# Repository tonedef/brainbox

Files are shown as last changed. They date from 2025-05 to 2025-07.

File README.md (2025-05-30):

# Disclaimer
Please note! I am not a physcian, nor promising that this device will achieve  positive results of any kind, nor promising that it will do no harm, nor that the device will work exactly as intended. For example, it does use pulsing light/sound which may or may not adversely affect people with epilepsy or other neurological conditions. *Anyone* choosing to build or use this device in part or in full, should consult with their physician first. Anyone who builds or uses this device or utilizes any information presented here, agrees to assume *all* risks and responsibilities. DISCUSS ALL MEDICAL ISUES WITH YOUR PHYSICIAN FIRST

# What is Memini?
Memini is a simple device that produces 40Hz audio and light pulses designed to delay and slow the progression of Alzheimer's/dementia. It's based on promising research done at MIT: 
https://news.mit.edu/2022/small-studies-40hz-sensory-stimulation-confirm-safety-suggest-alzheimers-benefits-1213 (again, I cannot ensure that this will happen.  There are ongoing clinic trials for this, and I have no guarantee that the designs here will be able to achieve that)

It's meant to be as simple as possible for anyone to use. A dimmer to control how bright the light is, a volume control for the sound, and a single button to start/stop the device. It also has a web interface accessible thru WiFi, and the code can be upgraded/modified to support all kinds of things such as:
- making it an alarm clock, so that it runs without user intervention
- tracking usage
- playing reminders for other mental activities
- Repurposing for anything else that could use a couple of buttons and a mono audio output

The MCU being used is a Wemos S2 mini board. While you can use a Wemos C3, or an older D1 (code changes required), the S2 is ideal, as it includes a DAC output which makes it easy to modify the existing on/off square wave audio pulse to support significantly more audio options thru software upgrades.

It's designed using pre-built dev boards and a few through-hole components to make it easy for hobbyists to make. The most challanging thing to build will be the housing, but really anything box like can be used for that.

# Getting started
Aquire the components.

## Electronic component BOM

- 1x PCB board. Send the grb_v_x_x.zip to your PCB mfg. This is the latest confirmed [build](https://github.com/tonedef/Memini/blob/main/KiCad/40Hz_S2/grb_v_0_3.zip)
- 1x [Wemos S2 mini](https://www.amazon.com/HiLetgo-ESP32-S2FN4R2-ESP32-S2-Type-C-Connect/dp/B0B291LZ99)
- 1x  N-Channel logic level MOSFET [CSD19531KCS](https://www.digikey.com/en/products/detail/texas-instruments/CSD19531KCS/4437459). If you're using a short LED strip (< 400mm), you can get away with generic MOSFETs, like the ubiquitous [IRF540](https://www.amazon.com/dp/B0CBKGPJML), which I've tried sucessfully.
- 1x 100 Ohm resistor a [kit](https://www.amazon.com/Resistors-Assortment-Electronic-Components-Experiments/dp/B09SFCF5XY/) is probably the best bet for this if you don't have one already
- 1x 10k Ohm resistor a [kit](https://www.amazon.com/Resistors-Assortment-Electronic-Components-Experiments/dp/B09SFCF5XY/) is probably the best bet for this if you don't have one already
- 1x 1n4007 Diode. Again, a [kit](https://www.amazon.com/HiLetgo-100pcs-Schottky-Rectifier-Assorted/dp/B07VHMCJK1/) if you don't have one already
- 1x 10k Ohm 15mm PCB vertical [potentiometer](https://www.amazon.com/dp/B0DN1DHWLR).
- 1x 20mm Rotary [encoder](https://www.amazon.com/dp/B07D3DF8TK) (with or without switch). 
- 1x 0.96in 4 pin [I2C display](https://www.amazon.com/MakerFocus-Display-Communication-SSD1315-Raspberry/dp/B0DR2CMYGM)
- 1x PAM8302 [audio dev board](https://www.amazon.com/Audio-Development-Tools-Adafruit-Amplifier/dp/B00PY2YSI4)
- 5V [LED strip](https://www.amazon.com/dp/B0DPKMQNJJ) (pay attention to the Voltage, most are 12V). You can use any color, but I'd recommend a warm white like 3000K.
- 2x 6×6×9mm [Momentary Tactile Tact Push Button Switches](https://www.amazon.com/dp/B07CGCPGPT?th=1)
- 1x Small 4 Ohm [speaker](https://www.amazon.com/dp/B0CCP2Q168)
- 1x [5V power supply](https://www.amazon.com/100-240V-Extension-Replacement-5-5x2-5mm-Security/dp/B0DGFSQS97) walwart
- 1x DC [jack](https://www.amazon.com/dp/B07CTCLKPP) that fits your 5V walwart
- 2x M2x6mm standoffs. A [kit](https://www.amazon.com/300pcs-Standoff-Column-Spacer-Assortment/dp/B07B9X1KY6/) is good, if you don't have one already.
- Assorted 2.54mm male and female [headers](https://www.amazon.com/dp/B0774VBJ3J) (most/all of these should already be included in the components above). You can of course use [JTS-XH](https://www.amazon.com/Taiss-560PCS-Connector-Adapter-Housing/dp/B09ZTWCZ3K) connectors for the power in, LED out, and  audio out, or just wire them directly.
 
 ## Case
 There's plenty of ways to do this. The easiest is to just a get a cast acrylic box that's roughly 4"x4"x4" and has roughly 1/8" (3mm) thick walls. I simply made boxes out of wood I had lying around, and grabbed a cheap piece of 1/8" scrap cast acrylic from TAP Plastics for the face plate. Cast acrylic usually has a paper backing as opposed to a plastic film. Cast acrylic is generally easier to machine.

 # Assembly
 ## software
 You will need to know how to connect your Wemos S2 to your PC and upload the code to it. There are plenty of tutorials on how to do this. The board needs to be in the [DFU mode](https://www.wemos.cc/en/latest/tutorials/s2/get_started_with_arduino_s2.html) to get picked up, and you need the espressif boards in your Arduino IDE, along with a bunch of libraries:
 - ESP32 boards [installation](https://randomnerdtutorials.com/installing-the-esp32-board-in-arduino-ide-windows-instructions/)
 - ezButton (library from ArduinoGetStarted.com)
 - ESP Rotary (library from Lennart Hennigs)
 - Adafruit_GFX (library from Adafruit)
 - Adafruit_SSD1306 (library from Adafruit)
  
  Libraries are installed thru the Arudino IDE interface. It's been a while since I installed the things I need, so my appologies if I've missed anything. If you get errors, it should point to what's missing, and you'll have to  look for it and install the library.

  ## hardware (main board)
  - install the female headers for the Wemos board
  - dry fit the male pins to the audio dev board and the PCB (don't solder just yet)
  - solder the male pins to all the dev boards (Wemos, audio, and display). DON'T solder to any of these to the PCB just yet, but do dry fit them to make sure the pins are properly aligned and adjust if needed.
  - if your using connectors for the power in, audio out, and LED out, solder them now
  - solder all the remaining components to the PCB except for the display
  - attach the standoffs to the display.
  - As the OLED 0.96 displays aren't fully standardized on pin placement and mounting holes, the PCB has generous sized mounting holes and pin pads. Fit the display on the PCB and align it.
  - screw in the display's attached standoffs to the PCB
  - keeping the display parallel to the PCB, solder the display pins to the PCB
 
 ## hardware (DC jack, LED, and speaker)

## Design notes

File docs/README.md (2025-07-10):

>[!IMPORTANT]
I am not a physician and make no guarantees about this device's effectiveness, safety, or intended function. It uses pulsing light and sound, which may pose risks for individuals with epilepsy or other neurological conditions. Anyone choosing to build or use this device, in whole or in part, should consult their physician beforehand. By engaging with this device or any related information, you accept full responsibility for all risks. Always discuss medical concerns with your doctor first.

# What is wavebox?
Wavebox is a simple device that produces 40Hz audio and light pulses designed to delay and slow the progression of Alzheimer's/dementia. It's based on promising research done at MIT: 
https://news.mit.edu/2022/small-studies-40hz-sensory-stimulation-confirm-safety-suggest-alzheimers-benefits-1213 

Again, I cannot ensure that this will happen. There are ongoing clinic trials for this, so the efficacy is still being evaluated.

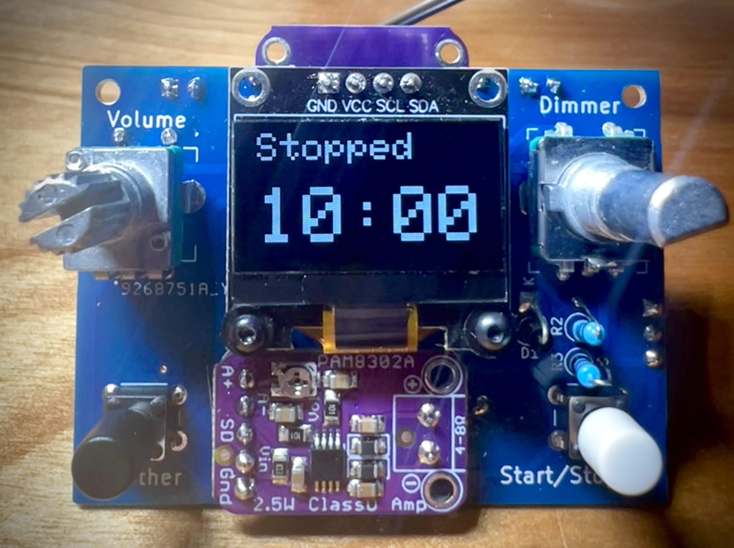
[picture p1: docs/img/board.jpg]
working board


It's meant to be as simple as possible for anyone to use. A dimmer to control how bright the light is, a volume control for the sound, and a single button to start/stop the device (though two other buttons, one on the encoder and one on left side exist for expansion or to repurpose this for any number of other uses, like a radio). It also has a web interface accessible thru WiFi, and the code can be upgraded/modified to support all kinds of things such as:
- making it an alarm clock, so that it runs without user intervention
- tracking usage
- playing reminders for other mental activities
- Repurposing for anything else that could use a couple of buttons and a mono audio output

The MCU being used is a Wemos S2 mini board. While you can use a Wemos C3, or an older D1 (significant code changes required), the S2 is ideal, as the GPIO pin being used to supply the PWM audio (which here is just a simple square wave), is also the DAC output. This makes it easy to switch over to an 8bit DAC output to support significantly more audio options thru software.

It's designed using pre-built dev boards and a few through-hole components to make it easy for hobbyists to make. The most challanging thing to build will be the housing, but really anything box like can be used for that.

# Getting started

## Electronic component BOM
Get all the necessary components for the electronics. You don't have to get the exact brand I've listed, but the values, and footprint of the component is important. I've made a few of these with generic no-name encoders and pots for example. The 0.96" I2C displays all seem to have slight variations in hole/pin placements, which I've tried to account for in the PCB's mounting and through-hole pads.

- 1x PCB board. Send the grb_v_x_x.zip to your PCB mfg. This is the latest confirmed [build](https://github.com/tonedef/wavebox/blob/main/KiCad/40Hz_S2/grb_v_0_3.zip). Also happy to orchestrate a group buy if folks are interested (minimum order is usually 5)
- 1x [Wemos S2 mini](https://www.amazon.com/HiLetgo-ESP32-S2FN4R2-ESP32-S2-Type-C-Connect/dp/B0B291LZ99)
- 1x  N-Channel MOSFETs [IRF540](https://www.amazon.com/dp/B0CBKGPJML) .
- 1x 100 Ohm resistor. A [kit](https://www.amazon.com/dp/B07L851T3V/ref=sspa_dk_detail_0) is probably the best bet for this if you don't have one already
- 1x 10k Ohm resistor (would be in the kit above)
- 1x 1n4007 Diode. Again, a [kit](https://www.amazon.com/HiLetgo-100pcs-Schottky-Rectifier-Assorted/dp/B07VHMCJK1/) if you don't have one already
- 1x 10k Ohm 15mm PCB vertical [potentiometer](https://www.amazon.com/dp/B0DN1DHWLR).
- 1x 20mm Rotary [encoder](https://www.amazon.com/dp/B07D3DF8TK) (with or without switch). 
- 1x 0.96in 4 pin [I2C display](https://www.amazon.com/MakerFocus-Display-Communication-SSD1315-Raspberry/dp/B0DR2CMYGM)
- 1x PAM8302 [audio dev board](https://www.amazon.com/Audio-Development-Tools-Adafruit-Amplifier/dp/B00PY2YSI4)
- 5V [LED strip](https://www.amazon.com/dp/B0DPKMQNJJ) (pay attention to the Voltage, most are 12V). You can use any color, but I'd recommend a warm white like 3000K.
- 2x 6x6x12 Momentary tactile [buttons](https://www.amazon.com/uxcell-6x6x12mm-Momentary-Tactile-Button/dp/B07JLV6WSF/)
- 1x Box of [caps](https://www.amazon.com/Tactile-Button-Plastic-Replacement-Breadboard/dp/B0B52B8S63) (don't need a whole box, but aren't really sold individually usually)
- 1x Small 4 Ohm [speaker](https://www.amazon.com/dp/B0CCP2Q168) (8ohm should also work)
- 1x [5V power supply](https://www.amazon.com/100-240V-Extension-Replacement-5-5x2-5mm-Security/dp/B0DGFSQS97) walwart. You can also just use the USB-C connector on the Wemos S2 mini, which is great for easy reprogramming, but limits the amperage you can draw on the LED out (only an issue if you need more than ~500mA). 
- 1x DC [jack](https://www.amazon.com/dp/B07CTCLKPP) that fits your 5V walwart

- 2x M2x6mm standoffs. A [kit](https://www.amazon.com/300pcs-Standoff-Column-Spacer-Assortment/dp/B07B9X1KY6/) is good, if you don't have one already.
- Assorted 2.54mm male and female [headers](https://www.amazon.com/dp/B0774VBJ3J) (most/all of these should already be included in the components above). You can of course use [JTS-XH](https://www.amazon.com/Taiss-560PCS-Connector-Adapter-Housing/dp/B09ZTWCZ3K) connectors for the power in, LED out, and  audio out, or just wire them directly.
 
 ## Case
 There's plenty of ways to do this. The easiest is to just a get a cast acrylic box that's roughly 4"x4"x4" and has roughly 1/8" (3mm) thick walls. I simply made boxes out of wood I had lying around, and grabbed a cheap piece of 1/8" scrap cast acrylic from TAP Plastics for the face plate. Cast acrylic usually has a paper backing as opposed to a plastic film. Cast acrylic is generally easier to machine.

 # Assembly
 ## software
 You will need to know how to connect your Wemos S2 to your PC and upload the code to it. There are plenty of tutorials on how to do this. The board needs to be in the [DFU mode](https://www.wemos.cc/en/latest/tutorials/s2/get_started_with_arduino_s2.html) to get picked up, and you need the espressif boards in your Arduino IDE, along with a bunch of libraries:
 - ESP32 boards [installation](https://randomnerdtutorials.com/installing-the-esp32-board-in-arduino-ide-windows-instructions/)
 - ezButton (library from ArduinoGetStarted.com)
 - ESP Rotary (library from Lennart Hennigs)
 - Adafruit_GFX (library from Adafruit)
 - Adafruit_SSD1306 (library from Adafruit)
  
  Libraries are installed thru the Arudino IDE interface. It's been a while since I installed the things I need, so my appologies if I've missed anything. If you get errors, it should point to what's missing, and you'll have to  look for it and install the library.

  ## hardware (main board)
  - install the female headers for the Wemos board
  - solder the male pins to all the dev boards (Wemos, audio, and display). DON'T solder to any of these to the PCB just yet, but do dry fit them to make sure the pins are properly aligned and adjust if needed.
  - if your using connectors for the power in, audio out, and LED out, solder them now
  - solder all the remaining components, including the female headers for the Wemos board, to the PCB except for the display
  - attach the standoffs to the display.
  - As the OLED 0.96 displays aren't fully standardized on pin placement and mounting holes, the PCB has generous sized mounting holes and pin pads. Fit the display on the PCB and align it.
  - screw in the display's attached standoffs to the PCB
  - keeping the display parallel to the PCB, solder the display pins to the PCB (they may not protrude all the way thru the board, but that's fine)
 
 ## hardware (front panel)
  - any material can be used, but the easiest is a 1/8" thick 4x4" piece of clear cast acrylic.
  - [SVG and PDF](https://github.com/tonedef/wavebox/tree/main/images) faceplates can either be printed to guide manual cutting or used in CAD for CNC
  - note: the faceplate has offset mounting as opposed to the corners, so that you're not screwing the faceplate into a 45 joint of the housing, assuming you're making this out of wood with faces cut at a 45 degree bevel

 ## hardware (housing)
  - 3/4" 4x18" wood board works
  - cut 4, 4x4 sections at a 45 degree bevel
  - set a bit or a blade to 3/8" deep and run one side of all four sections about 1/8" in from the edge (this will make a 1/8" inset for your faceplate) 
  - in the center of one of the 4x4 pieces, cut a hole for the speaker (check the diameter you need for your speaker, it should be about 2")
  - on the same board as the speaker, cut a small 1/8 hole or so for the LED wires about 1/2 from the top edge in line with the center of the speaker
  - on the same board as the speaker, at the opposite end of the LED hole, cut a mount hole for your DC plug or a slot for a USB cable (if you plan to inset a bottom face into the box, leave enough room to accomodate your plug/cable)
  - glue and/or nail all four boards together so they form a box
  - finish the box however you like

 ## hardware (DC jack, LED, and speaker)
  - leaving the tape on, wrap the LED strip around the top edge of the box and cut the strip at the nearest cut point where the strip doesn't overlap
  - attach wire leads to the LED strip, the DC jack (if using), and the speaker, make them long enough to attach to the PCB with room to spare so you can connect everything easily
  - feed the LED leads thru the hole cut for the LED wires
  - take the tape off the LED strip and tape the strip around the box, then lift up each end of the strip, apply a drop of superglue and press them back down (most tape backings don't hold long term)
  - attach speaker and DC jack to box
  - attach leads to the PCB board
  - attach faceplat to PCB board, and then attach the faceplate to the box

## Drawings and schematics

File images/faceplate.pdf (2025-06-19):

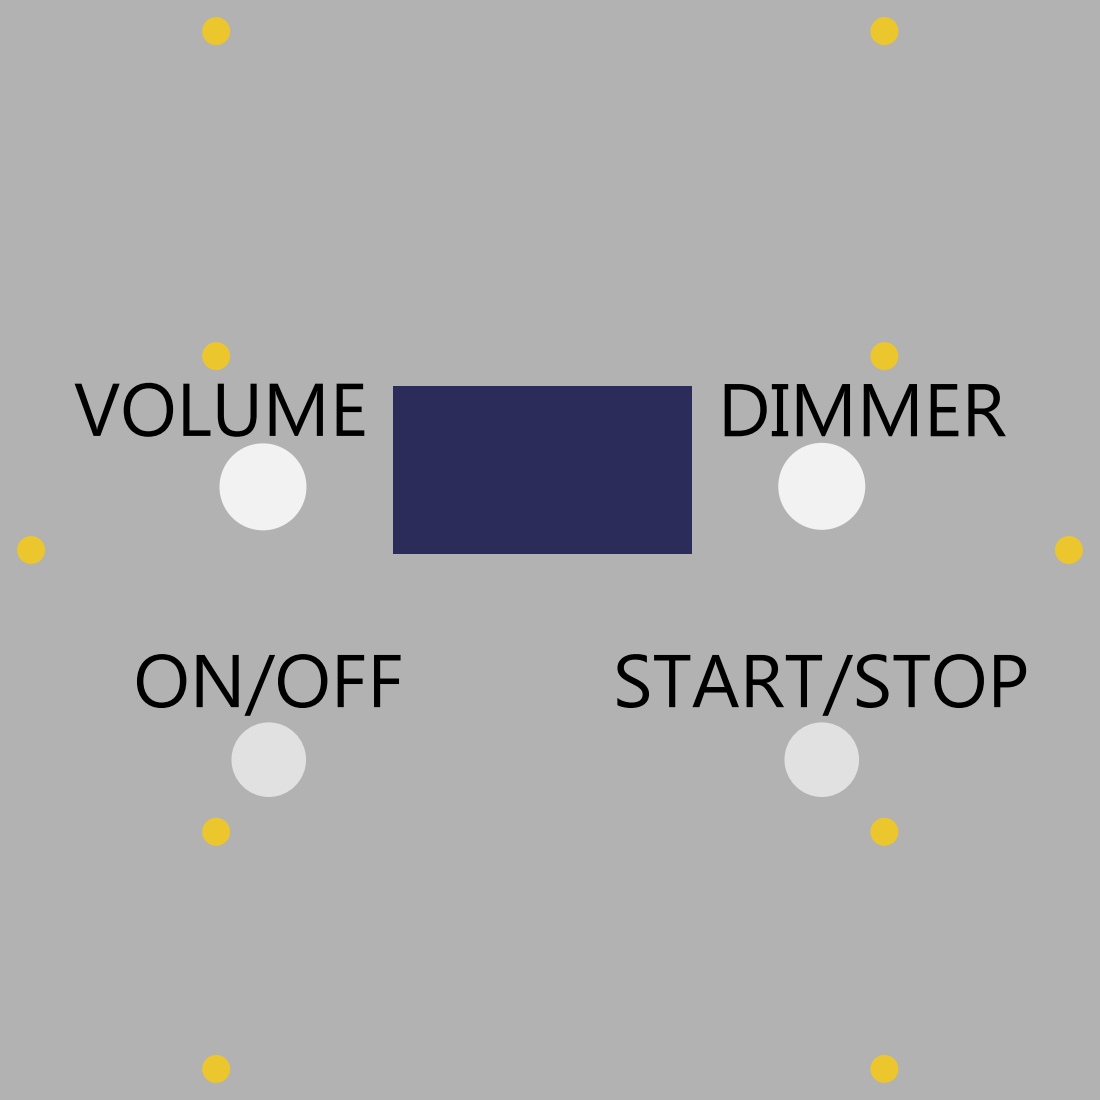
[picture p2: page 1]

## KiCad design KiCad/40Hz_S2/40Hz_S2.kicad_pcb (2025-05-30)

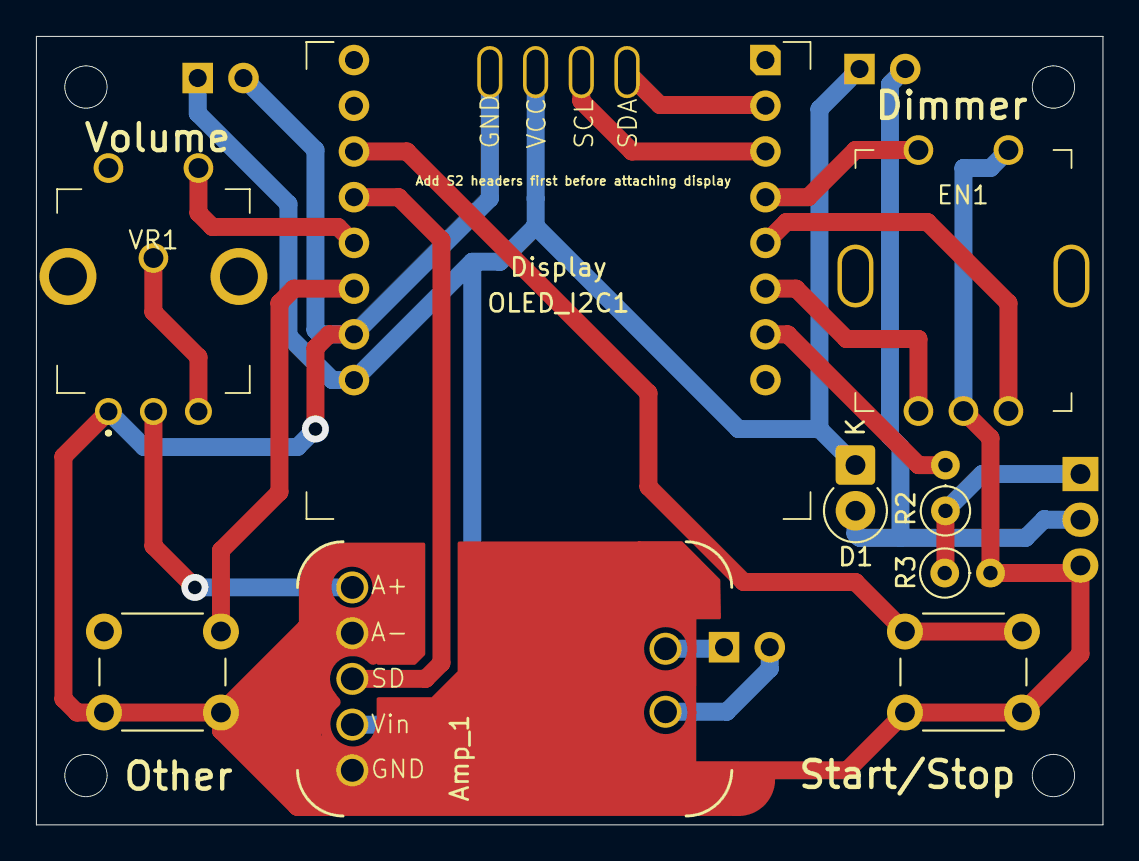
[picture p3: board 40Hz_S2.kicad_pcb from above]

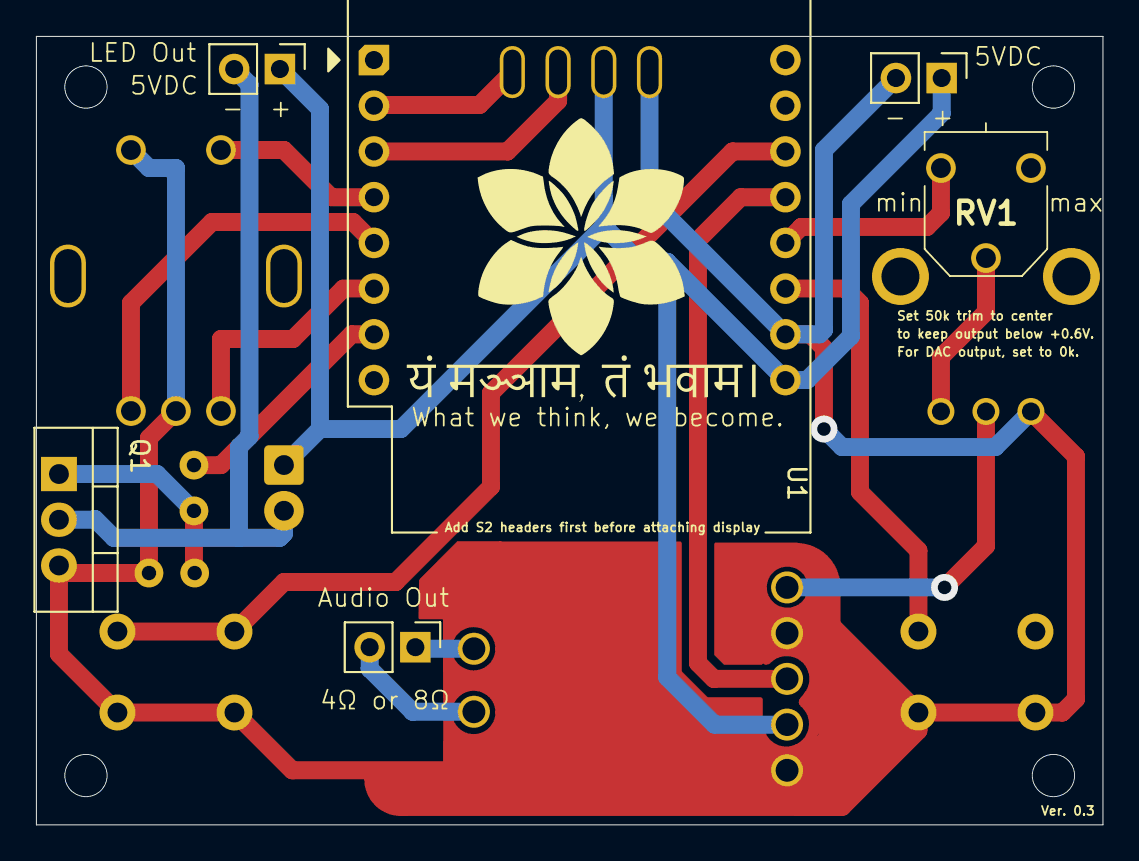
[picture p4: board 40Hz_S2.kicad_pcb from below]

Board: 2 copper layers, 59.2 x 43.8 mm, 15 parts (6 on the bottom side), 18 nets.

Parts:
Amp_1: PAM8302_adafruit
D1: 1N4007; D_DO-41_SOD81_P2.54mm_Vertical_KathodeUp
EN1: Encoder; encoder_20mm_switch
J1: PWR; PinHeader_1x02_P2.54mm_Vertical
J2: Audio; PinHeader_1x02_P2.54mm_Vertical
J3: LED; PinHeader_1x02_P2.54mm_Vertical
OLED_I2C1: Display; OLED_display_I2C_0_96in
Q1: CSD19531KCS; TO-220-3_Vertical
R2: 100; R_Axial_DIN0207_L6.3mm_D2.5mm_P2.54mm_Vertical
R3: 10K; R_Axial_DIN0207_L6.3mm_D2.5mm_P2.54mm_Vertical
RV1: R_Potentiometer_Trim_US; 3306F1103
U1: WeMos_S2_mini; WEMOS_S2_mini_no_inner_row
VR1: 10K Pot; potentiometer_vert_no_switch
other1: Start/Stop; SW_PUSH_6mm_H9.5mm
start/stop1: Start/Stop; SW_PUSH_6mm_H9.5mm

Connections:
5V: Amp_1.4 (Vin), D1.1 (K), J1.1, J3.1, OLED_I2C1.Vcc, U1.9 (VBUS)
Audio: RV1.3, U1.12 (IO18)
Btn1: U1.14 (IO35), start/stop1.1
Btn2: EN1.1, U1.4 (IO7)
Btn3: U1.11 (IO16), other1.1
Enc_A: EN1.A1 (A), U1.6 (IO11)
Enc_B: EN1.B1 (B), U1.5 (IO9)
GND: Amp_1.2 (A-), Amp_1.5 (GND), EN1.2, EN1.GND, J1.2, OLED_I2C1.GND, Q1.3 (S), R3.2, U1.10 (GND), VR1.1, other1.2, start/stop1.2
LED: R2.2, U1.7 (IO12)
unnamed: Amp_1.1 (A+), VR1.2
unnamed: Amp_1.7 (SPK+), J2.2
unnamed: Amp_1.6 (SPK-), J2.1
unnamed: D1.2 (A), J3.2, Q1.2 (D)
unnamed: Q1.1 (G), R2.1, R3.1
unnamed: RV1.2, VR1.3
SCL: OLED_I2C1.SCL, U1.3 (IO5)
SD: Amp_1.3 (SD), U1.13 (IO33)
SDA: OLED_I2C1.SDA, U1.2 (IO3)

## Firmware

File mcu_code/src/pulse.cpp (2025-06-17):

#include "PreferencesManager.h"
#include "shared_variables.h"
#include "pulse.h"
#include <Arduino.h>

#define AUDIO_TIMER LEDC_TIMER_0
#define AUDIO_MODE LEDC_LOW_SPEED_MODE
#define AUDIO_OUTPUT_IO 18
#define AUDIO_SD_IO 33
#define AUDIO_CHANNEL LEDC_CHANNEL_0
#define AUDIO_DUTY_RES LEDC_TIMER_13_BIT

#define LED_TIMER LEDC_TIMER_1
#define LED_MODE LEDC_LOW_SPEED_MODE
#define LED_OUTPUT_IO 12
#define LED_CHANNEL LEDC_CHANNEL_1
#define LED_DUTY_RES LEDC_TIMER_13_BIT

bool audio_initialized = false;
bool led_initialized = false;

/**
 * @brief Sets up the initial pin mode for the audio shutdown control pin.
 * The audio output is initially disabled (LOW).
 */
void setupPulse() {
  pinMode(AUDIO_SD_IO, OUTPUT);
  digitalWrite(AUDIO_SD_IO, LOW);
}


/**
 * @brief Configures and initializes an LEDC timer and channel for PWM output.
 * @param pin GPIO pin number for the PWM output.
 * @param duty Initial duty cycle value (0-8191 for 13-bit resolution).
 * @param frequency PWM frequency in Hz.
 * @param timer LEDC timer to use (e.g., LEDC_TIMER_0).
 * @param channel LEDC channel to use (e.g., LEDC_CHANNEL_0).
 * @param res Duty cycle resolution (e.g., LEDC_TIMER_13_BIT).
 */
void pulseInit(int pin, int duty, uint32_t frequency, ledc_timer_t timer, ledc_channel_t channel, ledc_mode_t mode, ledc_timer_bit_t res) {
  ledc_timer_config_t ledc_timer = {
    .speed_mode = mode,
    .duty_resolution = res,
    .timer_num = timer,
    .freq_hz = frequency,
    .clk_cfg = LEDC_AUTO_CLK
  };
  ESP_ERROR_CHECK(ledc_timer_config(&ledc_timer));

  ledc_channel_config_t ledc_channel = {
    .gpio_num = pin,
    .speed_mode = mode,
    .channel = channel,
    .intr_type = LEDC_INTR_DISABLE,
    .timer_sel = timer,
    .duty = 0,
    .hpoint = 0
  };
  ESP_ERROR_CHECK(ledc_channel_config(&ledc_channel));
}

/**
 * @brief Updates the audio and LED outputs based on the current playback state.
 * If playing, the outputs are enabled and configured according to current settings.
 * If not playing, outputs are disabled. Saves LED duty cycle to preferences when stopping playback.
 */
void updateOutputs(bool forceInit) {
  if (playing) {
    if (!audio_initialized || forceInit) {
      pulseInit(AUDIO_OUTPUT_IO, audio_duty, audio_frequency, AUDIO_TIMER, AUDIO_CHANNEL, AUDIO_MODE, AUDIO_DUTY_RES);
      audio_initialized = true;
    }
    if (!led_initialized || forceInit) {
      pulseInit(LED_OUTPUT_IO, led_duty, led_frequency, LED_TIMER, LED_CHANNEL, LED_MODE, LED_DUTY_RES);
      led_initialized = true;
    }

    // Set duty and update duty for AUDIO
    ESP_ERROR_CHECK(ledc_set_duty(AUDIO_MODE, AUDIO_CHANNEL, audio_duty));
    ESP_ERROR_CHECK(ledc_update_duty(AUDIO_MODE, AUDIO_CHANNEL));

    // Set duty and update duty for LED
    ESP_ERROR_CHECK(ledc_set_duty(LED_MODE, LED_CHANNEL, led_duty));
    ESP_ERROR_CHECK(ledc_update_duty(LED_MODE, LED_CHANNEL));
    digitalWrite(AUDIO_SD_IO, HIGH);
  } else {
    // Deactivate outputs.
    digitalWrite(AUDIO_SD_IO, LOW);

    if (audio_initialized) {
      ledc_stop(AUDIO_MODE, AUDIO_CHANNEL, 0);
      // Setting pins to INPUT and LOW when deactivating PWM.
      // This is done to avoid any residual output or power draw.
      pinMode(AUDIO_OUTPUT_IO, INPUT);
      digitalWrite(AUDIO_OUTPUT_IO, LOW);
      audio_initialized = false;
    }
    if (led_initialized) {
      ledc_stop(LED_MODE, LED_CHANNEL, 0);
      pinMode(LED_OUTPUT_IO, INPUT);
      digitalWrite(LED_OUTPUT_IO, LOW);
      led_initialized = false;
    }

    // Save the LED duty cycle if it's changed. Do on stop to save on writes
    if (led_duty != preferences.getInt("led_duty", DEFAULT_LED_DUTY)) {
      Serial.println("Saving!!");

      preferences.putInt("led_duty", led_duty);
    }
  }
}

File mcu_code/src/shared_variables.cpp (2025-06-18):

#include "shared_variables.h"

// Define default values
const int DEFAULT_AUDIO_DUTY = 328;                 ///< Default duty cycle for audio output.
const uint32_t DEFAULT_AUDIO_FREQUENCY = 40;        ///< Default frequency for audio output in Hz.
const int DEFAULT_LED_DUTY = 256;                   ///< Default duty cycle for LED output.
const uint32_t DEFAULT_LED_FREQUENCY = 40;          ///< Default frequency for LED output in Hz.
const char* DEFAULT_AP_SSID = "wavebox";            ///< Default SSID when the device is in Access Point mode.
const char* DEFAULT_AP_PASSWORD = "CHANGE_ME";      ///< Default password for the Access Point mode.
const char* DEFAULT_STA_SSID = "";                  ///< Default SSID for Station mode if not found in preferences.
const char* DEFAULT_STA_PASSWORD = "";              ///< Default password for Station mode if not found in preferences.
const int DEFAULT_MAX_TIME = (30 * 60 * 1000);      ///< Default maximum session time in milliseconds (30 minutes).
const float VERSION = 0.30;                         ///< Firmware version number.

// Initialize shared variables with default values
char wifi_ap_ip[16];                                ///< Buffer to store the IP address when in AP mode.
int audio_duty = DEFAULT_AUDIO_DUTY;                ///< Current duty cycle for audio output.
uint32_t audio_frequency = DEFAULT_AUDIO_FREQUENCY; ///< Current frequency for audio output.
int led_duty = DEFAULT_LED_DUTY;                    ///< Current duty cycle for LED output.
uint32_t led_frequency = DEFAULT_LED_FREQUENCY;     ///< Current frequency for LED output.
int max_time = DEFAULT_MAX_TIME;                    ///< Current maximum session time in milliseconds.
bool playing = false;                               ///< Flag indicating if playback is active.
bool display_sleep = false;                         ///< Flag indicating if display auto-sleep is enabled.
bool show_display = true;                           ///< Flag indicating if the display should be active (not asleep).
String LOCAL_STA_SSID;                              ///< SSID for the current Station mode WiFi connection, loaded from Preferences.
String LOCAL_STA_PASSWORD;                          ///< Password for the current Station mode WiFi connection, loaded from Preferences.

// Raw bitmap data
const uint8_t PROGMEM LOGO[] = {
  0x01, 0xfc, 0x00, 0x02, 0x00, 0x0f, 0x00, 0x00, 0x00, 0x00, 0x00, 0x00, 0x00, 0x00, 0x00, 0x00, 
  0x07, 0xfe, 0x00, 0x07, 0x00, 0x1f, 0x80, 0x00, 0x00, 0x00, 0x00, 0x00, 0x00, 0x00, 0x00, 0x00, 
  0x1e, 0x0f, 0x00, 0x07, 0x00, 0x3f, 0x80, 0x00, 0x00, 0x00, 0x00, 0x00, 0x00, 0x00, 0x00, 0x00, 
  0x38, 0x07, 0x80, 0x0f, 0x00, 0x7f, 0x80, 0x00, 0x00, 0x00, 0x00, 0x00, 0x00, 0x00, 0x00, 0x00, 
  0x30, 0x07, 0x80, 0x0f, 0x00, 0xf0, 0x00, 0x00, 0x00, 0x00, 0x00, 0x00, 0x00, 0x00, 0x00, 0x00, 
  0x60, 0x03, 0x80, 0x1f, 0x00, 0xe0, 0x00, 0x00, 0x00, 0x00, 0x00, 0x00, 0x00, 0x00, 0x00, 0x00, 
  0x60, 0x03, 0x80, 0x1e, 0x01, 0xc0, 0x00, 0x00, 0x00, 0x00, 0x00, 0x00, 0x00, 0x00, 0x00, 0x00, 
  0xc0, 0x03, 0x80, 0x3e, 0x01, 0x80, 0x00, 0x00, 0x00, 0x00, 0x00, 0x00, 0x00, 0x00, 0x00, 0x00, 
  0xc1, 0x83, 0x80, 0x3e, 0x03, 0x80, 0x00, 0x00, 0x00, 0x00, 0x00, 0x00, 0x00, 0x00, 0x00, 0x00, 
  0xc3, 0xc3, 0x80, 0x7c, 0x03, 0x00, 0x00, 0x00, 0x00, 0x00, 0x03, 0x80, 0x00, 0x00, 0x00, 0x00, 
  0xc3, 0xc3, 0x80, 0x7c, 0x06, 0x00, 0x00, 0x00, 0x00, 0x00, 0x07, 0x80, 0x00, 0x00, 0x00, 0x00, 
  0xc3, 0xc3, 0x80, 0xfc, 0x06, 0x00, 0x00, 0x00, 0x00, 0x00, 0x07, 0x80, 0x00, 0x00, 0x00, 0x00, 
  0xe0, 0xc7, 0x80, 0xfc, 0x0c, 0x00, 0x00, 0x00, 0x00, 0x00, 0x07, 0x80, 0x00, 0x00, 0x00, 0x00, 
  0x71, 0x87, 0x81, 0xfc, 0x0c, 0x00, 0x00, 0x00, 0x00, 0x00, 0x0f, 0x00, 0x00, 0x00, 0x00, 0x00, 
  0x3f, 0x87, 0x81, 0x7c, 0x18, 0x00, 0x00, 0x00, 0x00, 0x00, 0x0f, 0x00, 0x00, 0x00, 0x00, 0x00, 
  0x1e, 0x07, 0x03, 0x78, 0x18, 0x00, 0x00, 0x00, 0x00, 0x00, 0x0e, 0x00, 0x00, 0x00, 0x00, 0x00, 
  0x00, 0x07, 0x02, 0x78, 0x10, 0x00, 0x00, 0x00, 0x00, 0x00, 0x1e, 0x00, 0x00, 0x00, 0x00, 0x00, 
  0x00, 0x07, 0x06, 0x78, 0x30, 0x00, 0x00, 0x00, 0x00, 0x00, 0x1e, 0x00, 0x00, 0x00, 0x00, 0x00, 
  0x00, 0x0f, 0x06, 0x78, 0x30, 0x00, 0x00, 0x00, 0x00, 0x00, 0x1c, 0x00, 0x00, 0x00, 0x00, 0x00, 
  0x00, 0x0f, 0x0c, 0x78, 0x60, 0x00, 0x00, 0x00, 0x00, 0x00, 0x3c, 0x00, 0x00, 0x00, 0x00, 0x00, 
  0x00, 0x0f, 0x0c, 0x78, 0x60, 0x7b, 0x80, 0xc3, 0x00, 0xf0, 0x38, 0x60, 0x1e, 0x00, 0x00, 0x00, 
  0x00, 0x0e, 0x18, 0xf0, 0x41, 0xff, 0x81, 0xc7, 0x83, 0xf8, 0x38, 0xf0, 0x7f, 0x00, 0x78, 0x60, 
  0x00, 0x0e, 0x18, 0xf0, 0xc3, 0x8f, 0x81, 0xc7, 0x87, 0x98, 0x78, 0xf0, 0xf3, 0x80, 0xf9, 0xf0, 
  0x00, 0x1e, 0x30, 0xf0, 0x87, 0x0f, 0x83, 0xc7, 0x8f, 0x18, 0x70, 0xf1, 0xe3, 0x81, 0x9f, 0xb0, 
  0x00, 0x1e, 0x30, 0xf1, 0x87, 0x0f, 0x03, 0x83, 0x9e, 0x38, 0x70, 0x73, 0xc3, 0xc3, 0x1f, 0x30, 
  0x00, 0x1e, 0x60, 0xf1, 0x8e, 0x0f, 0x03, 0x83, 0xfe, 0x70, 0xf0, 0x7f, 0x83, 0xc6, 0x1e, 0x00, 
  0x00, 0x1c, 0x60, 0xf3, 0x1c, 0x1e, 0x07, 0x03, 0xfc, 0xe0, 0xe0, 0x7f, 0x83, 0xcc, 0x1e, 0x02, 
  0x00, 0x1c, 0xc0, 0xe3, 0x1c, 0x1e, 0x0f, 0x03, 0x3f, 0xc1, 0xe0, 0x67, 0x01, 0xfc, 0x3c, 0x02, 
  0x00, 0x1c, 0xc0, 0xe6, 0x3c, 0x1e, 0x0f, 0x03, 0x3f, 0x01, 0xe0, 0x67, 0x01, 0xfc, 0x3c, 0x06, 
  0x00, 0x3d, 0x81, 0xe6, 0x38, 0x3e, 0x1e, 0x06, 0x3c, 0x03, 0xc0, 0xc7, 0x01, 0x80, 0x7c, 0x0c, 
  0x00, 0x3f, 0x01, 0xec, 0x38, 0x3c, 0x3e, 0x0c, 0x38, 0x07, 0xc1, 0x87, 0x01, 0x80, 0x78, 0x18, 
  0x00, 0x3f, 0x01, 0xec, 0x38, 0x7c, 0x7e, 0x1c, 0x38, 0x1d, 0xc3, 0x87, 0x03, 0x00, 0xf8, 0x38, 
  0x00, 0x3e, 0x01, 0xf8, 0x38, 0xfc, 0xee, 0x38, 0x1c, 0x39, 0xc7, 0x07, 0x87, 0x00, 0xd8, 0x70, 
  0x00, 0x3c, 0x01, 0xf0, 0x1f, 0x9f, 0xcf, 0xe0, 0x1f, 0xe1, 0xfc, 0x03, 0x8e, 0x01, 0xd8, 0xe0, 
  0x00, 0x38, 0x01, 0xe0, 0x1f, 0x0f, 0x07, 0x80, 0x07, 0xc0, 0xf0, 0x01, 0xfc, 0x73, 0x9f, 0x80, 
  0x00, 0x30, 0x01, 0xc0, 0x00, 0x00, 0x00, 0x00, 0x00, 0x00, 0x00, 0x00, 0xf8, 0x77, 0x0f, 0x00, 
  0x00, 0x00, 0x01, 0x00, 0x00, 0x00, 0x00, 0x00, 0x00, 0x00, 0x00, 0x00, 0x00, 0x7e, 0x00, 0x00, 
  0x00, 0x00, 0x00, 0x00, 0x00, 0x00, 0x00, 0x00, 0x00, 0x00, 0x00, 0x00, 0x00, 0x38, 0x00, 0x00
};

const uint8_t PROGMEM KNOB[] = {
	0x07, 0xc0, 0x18, 0x30, 0x20, 0x08, 0x40, 0x04, 0x40, 0x04, 0x83, 0x82, 0x84, 0x42, 0x85, 0x42, 
	0x84, 0x42, 0x83, 0x82, 0x40, 0x04, 0x50, 0x14, 0x30, 0x18, 0x70, 0x1c, 0x00, 0x00
};

/// @brief Defines the global instance of named bitmap assets.
const struct NamedBitmaps bitmaps = {
    {LOGO, 128, 38}, // .logo
    {KNOB, 15, 15}   // .knob
};

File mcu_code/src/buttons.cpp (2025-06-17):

#include "shared_variables.h"
#include "buttons.h"
#include "screen.h"
#include "pulse.h"
#include "timer.h"

#define START_STOP_PIN 35
#define ON_OFF_PIN 16
#define CONFIG_PIN 7
#define DEBOUNCE_TIME 50
#define HOLD_TIME 2000 // 2 seconds

ezButton startStopButton(START_STOP_PIN);
ezButton onOffButton(ON_OFF_PIN);
ezButton configButton(CONFIG_PIN);
DisplayState displayState;

ConfigsPage configPage;

static unsigned long buttonDownTime = 0; // Time when onOffButton was pressed
static bool longPress = false;   // Flag to indicate a potential long press on onOffButton

/**
 * @brief Initializes button pins, debounce times, and initial display state.
 * Sets up pull-up resistors for the buttons.
 */
void setupButtons() {
  displayState = NORMAL;

  pinMode(START_STOP_PIN, INPUT_PULLUP);
  startStopButton.setDebounceTime(DEBOUNCE_TIME);

  pinMode(ON_OFF_PIN, INPUT_PULLUP);
  onOffButton.setDebounceTime(DEBOUNCE_TIME);

  pinMode(CONFIG_PIN, INPUT_PULLUP);
  configButton.setDebounceTime(DEBOUNCE_TIME);
}

/**
 * @brief Handles the release event of the On/Off button.
 * Toggles the display's active state (`show_display`).
 * If display is turned off, playback is stopped and outputs are updated.
 */
void handleOnOff() {
  if (onOffButton.isReleased()) {
    displayState = NORMAL;
    playing = false;
    startTime = 0;
    show_display = !show_display;

    if (!show_display) {
      // Display is now OFF
      display.clearDisplay(); // Clear the screen
      display.display();      // Show the blank screen
      updateOutputs();
    } else {
      // Display is now ON
      statusDisplay(true);
    }
  }
}

/**
 * @brief Handles the release event of the Start/Stop button.
 * Toggles the playback state (`playing`).
 * Updates `startTime` for playback duration tracking.
 */
void handleStartStop() {
  if (startStopButton.isReleased()) {
    displayState = NORMAL;
    show_display = true;
    playing = !playing;
    
    if (playing) {
      startTime = millis();
    } else {
      startTime = 0;
    }

    updateOutputs();
    statusDisplay(true);
  }
}

/**
 * @brief Handles events for the Config button, including short and long presses.
 * Long press: Toggles between NORMAL and CONFIGS display states.
 * Short press (in CONFIGS state): Cycles through different configuration pages.
 */
void handleConfigs() {

  if (configButton.isPressed()) { // Button is currently held down
    if (!longPress) { // Button just went down
      longPress = true;
      buttonDownTime = millis();
    }
  }

  if (longPress && millis() - buttonDownTime >= HOLD_TIME) {
    show_display = true;
    if (playing) {
      playing = false;
      updateOutputs();
    }
    if (displayState == CONFIGS) {
      statusDisplay(true);
      displayState = ENTERING_NORMAL;
    } else if (displayState == NORMAL) {
      configPage = HOME;
      configsDisplay(configPage);
      displayState = ENTERING_CONFIGS;
    }

    longPress = false;
  }
  
  if (configButton.isReleased() && (displayState == ENTERING_CONFIGS || displayState == ENTERING_NORMAL)) {
    if (displayState == ENTERING_CONFIGS) {
      displayState = CONFIGS;

    } else if (displayState == ENTERING_NORMAL) {
      displayState = NORMAL;
    }
  } else if (configButton.isReleased() && displayState == CONFIGS) {
    switch (configPage) {
      case HOME:
        configPage = WiFi.status() != WL_CONNECTED ? WIFI_SETUP : APP_PAGE;
        break;
      case WIFI_SETUP:
        configPage = APP_PAGE;
        break;
      case APP_PAGE:
        // TODO: code up encoder changes to update time (change configPage = TIME_ADJ)
        configPage = HOME;
        break;
      case TIME_ADJ:
        // TODO: code up encoder changes to update time
        configPage = HOME;
        break;
    }
    configsDisplay(configPage);
  }
  
  if (configButton.isReleased()) {
    longPress = false;
  }
}

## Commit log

2025-05-16 Revamp code. Restructure. Add KiCad files
    [40Hz_S2-B_Cu.gbr, 40Hz_S2-B_Mask.gbr, 40Hz_S2-B_Paste.gbr, 40Hz_S2-B_Silkscreen.gbr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]
2025-05-30 updated grp files
    [40Hz_S2-B_Cu.gbr, 40Hz_S2-B_Mask.gbr, 40Hz_S2-B_Paste.gbr, 40Hz_S2-B_Silkscreen.gbr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]
2025-05-30 rename grb files with current ver no.
    [40Hz_S2-B_Cu.gbr, 40Hz_S2-B_Mask.gbr, 40Hz_S2-B_Paste.gbr, 40Hz_S2-B_Silkscreen.gbr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]
2025-06-12 rm dead code
    [40Hz_S2-NPTH.drl, 40Hz_S2-PTH.drl]
